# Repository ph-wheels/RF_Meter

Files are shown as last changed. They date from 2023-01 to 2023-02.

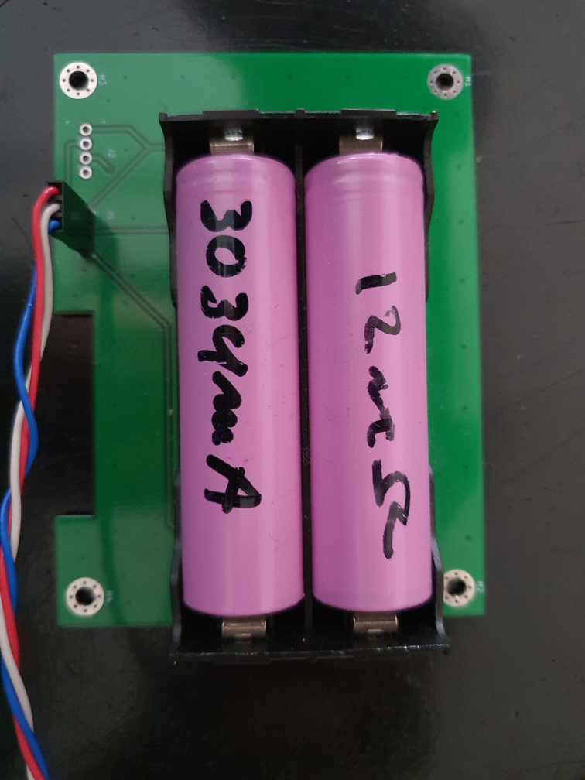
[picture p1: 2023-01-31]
images/battery_brd.png

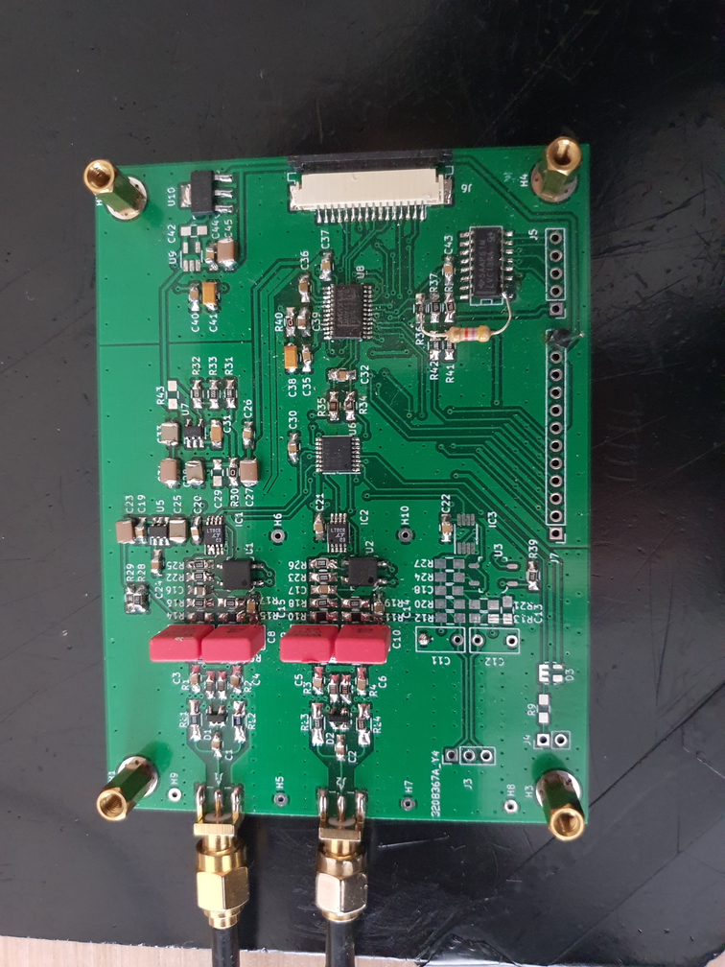
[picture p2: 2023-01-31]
images/adc_brd.png

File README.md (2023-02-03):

# RF_Meter
dual channel rf meter (work in progress)

This project started off with a question concerning replacement or source for
suitable detector diodes for the Boonton RF Millivolt meter quite a few months ago.
As a result of that, the idea was born to create a millivolt and/or power meter
using one of the modern ADC chips available today and since that time a few test
drawning and PCB where used in the process to the current V5 of the ADC board.
This project has been a combined effort with Jacques (ve2azx, http://www.ve2azx.net),
who already had developped a replacement board for the Boonton series of millivolt/
power meter as to fixed the issue with the mechanical chopper, without his valued
contribution, experiance, feedback and high precision RF measurement this project
would never exist.

The current design is based to 2 main PCB's and a battery board which also provides
some shielding to ADC board when mounted on top off it.

The control board consist of a connection to battery board, a flatcable connection
to ADC board and uart connection (ttl level) to external usb serial interface.
The board has and ESP32 MCU chip, which can be flashed via the USB serial interface,
will display info on the LCD screen (3.5" 480x240), monitors changes of the rotary
switch, touch screen, on-board push buttons and read/controls behaviour of the ADC
board. The RF Meter is battery powered and should be capable to provide adequate power
for several hours from 2x 2000 mAh or larger capacity batteries, optional board space
is provided to house a BMS unit and can be charged by the 2S 1A battery charger module
or via a barrel jack socket to deliver power via on-board regulator (3V3) to the MCU and
LCD screen.

The ADC board consist of 2 SMA and a flatcable connection to the control board,
optionally a connection to a 2 pin Amphenol connector, simular to the Boonton instruments.
This board holds 3 main area's being 3x input circuit, multiplexer with the ADC chip and the
voltages / reference sources with some control to switch attenuator and optional panel leds.
The input circuits for channels A/B are terminated with 50 Ohm followed by detector circuit
and attenuator, which is used to obtain a +23dBm range, into a differential low noise x1
amplifier, channel C (with it's components populated) only has the differential 5M6 resistors, the
attenuator and differential low noise x1 amplifier and is therefore not be a 50 Ohm input source.

Project status has been closed for now as we have finished our mean development goals being:
- a battery powered, using modern chips with large enough display making it a usable instrument
- a less than -55 dBm and up to +23 dBm input range
- a frequency range of less then 10 MHz upto in excess of 1 GHz
- an auto range mechanism in place over entire input range
- mechanism in place to load and maintain correction tables in none volatile memory

One area left for improvement is the option to obtain differential power reading between channel
B - A which kind of works (reasonably well within the lower 2 ranges) but will be slower in it's
update frequency then we expected it to be.

Future plans currently don't exist other then having an update schematic in place base on a dual
ADC chip approach which will speedup the channel B - A mode by factor 2x to 3x BUT this will yield
into a higher build cost due to extra ADC and the SSR / Mux chip.

Suggestion as how to build can be found in due time in folder 'Build' which will provide info and
steps to build the ADC and Control board and best practice to test and put each board into operation.

Paul	(PE1FCB (ex))

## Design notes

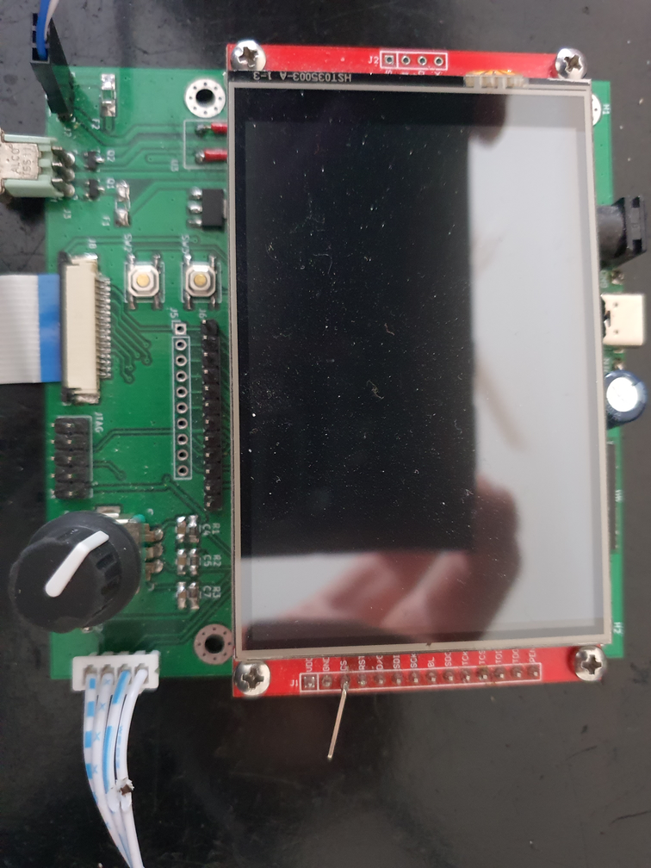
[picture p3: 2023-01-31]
images/control_display_brd.png

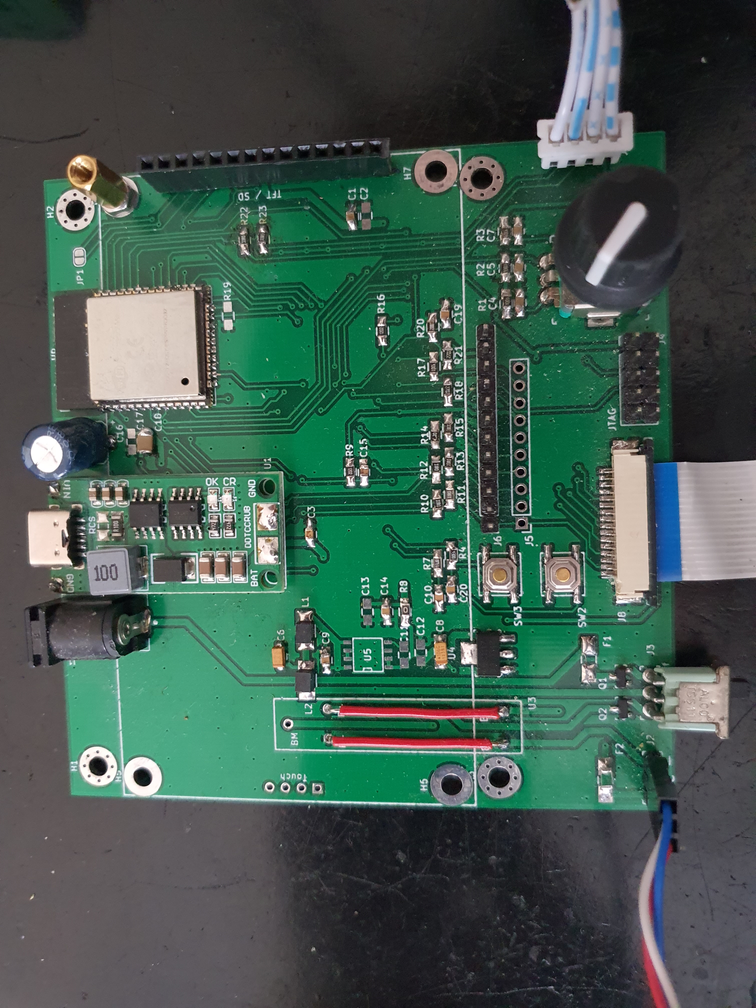
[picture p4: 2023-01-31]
images/control_brd.png

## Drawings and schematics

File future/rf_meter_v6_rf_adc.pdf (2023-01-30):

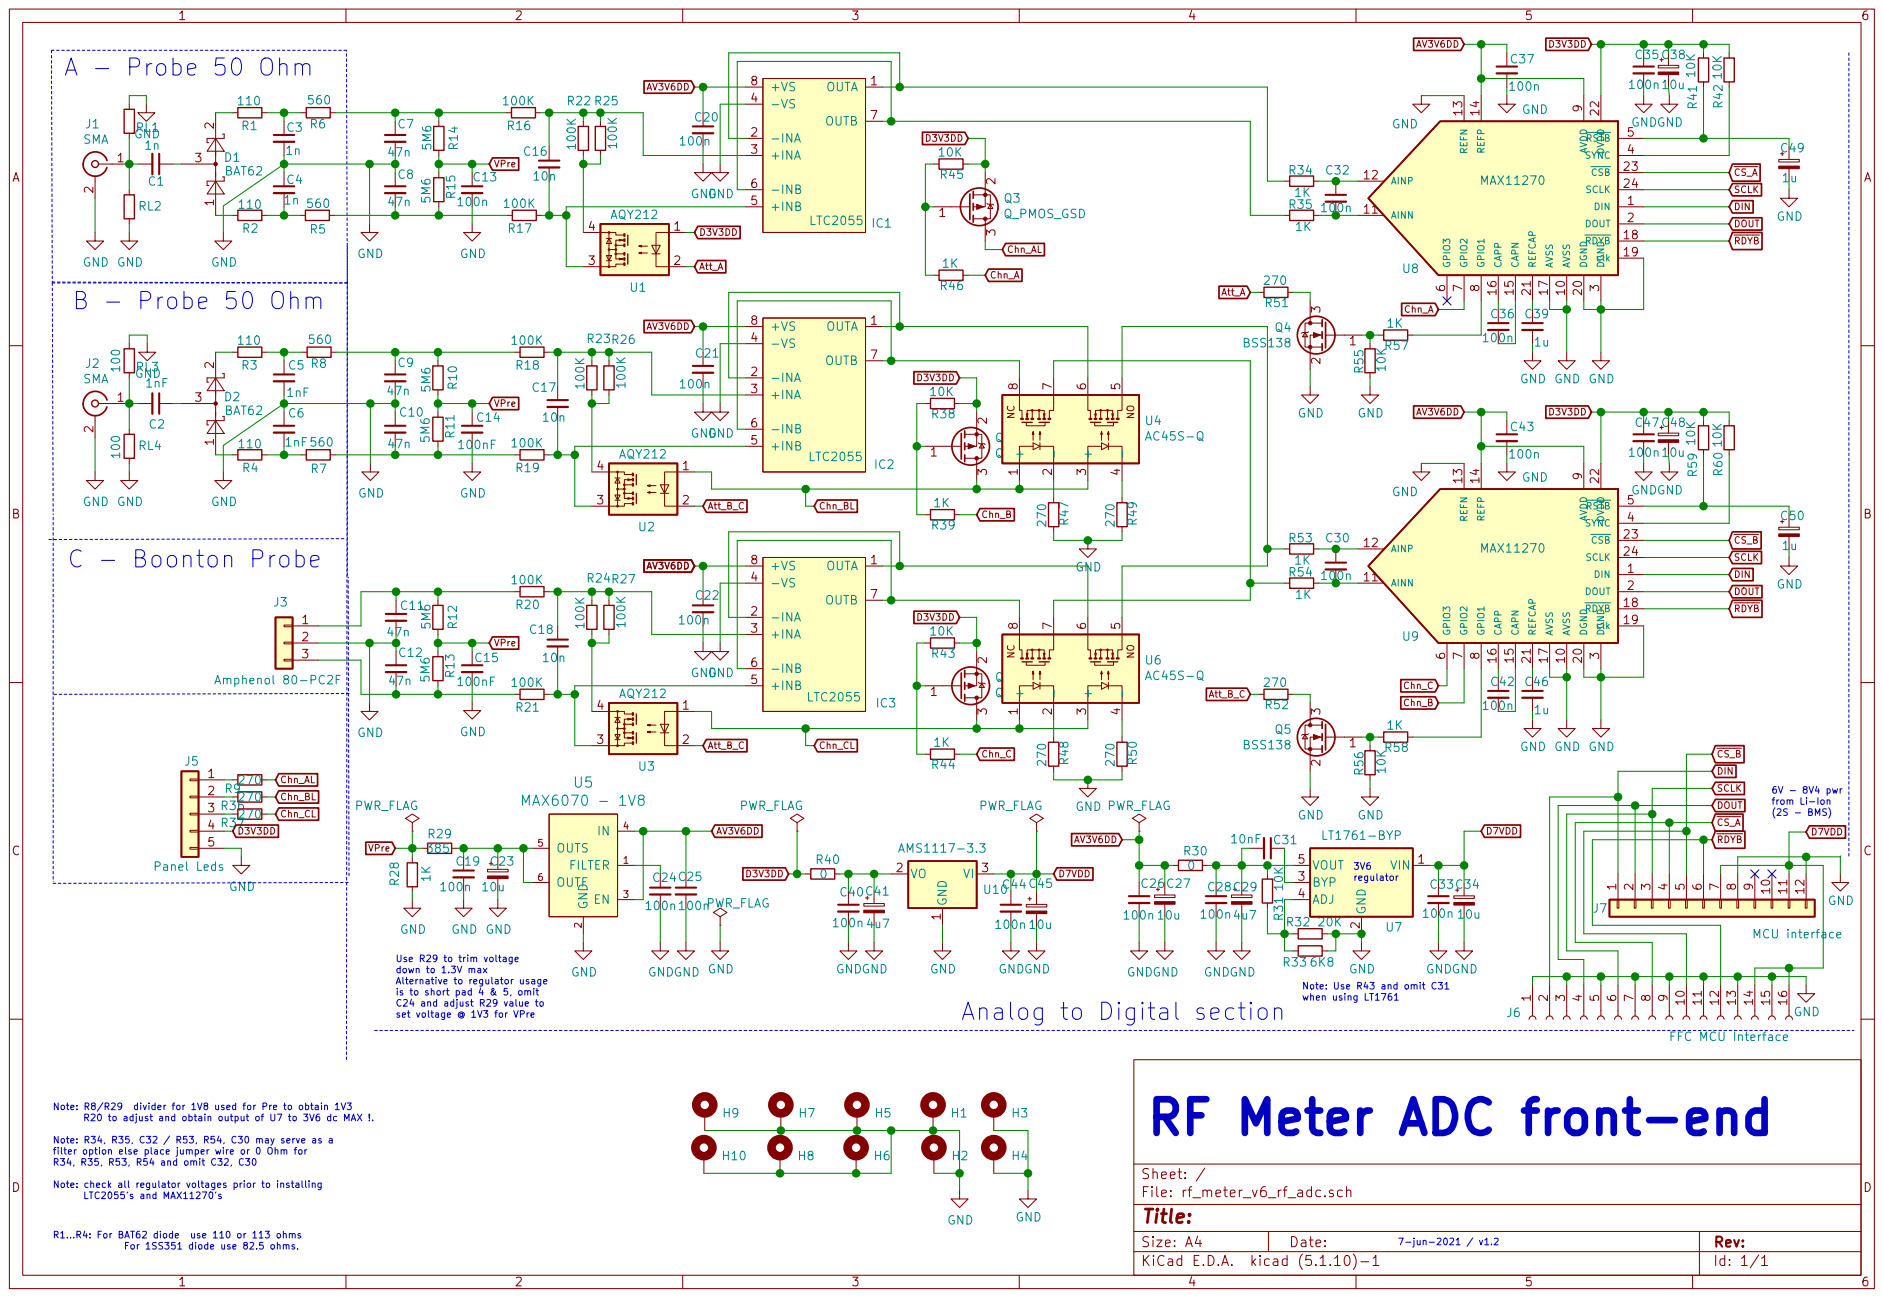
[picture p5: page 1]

7-jun-2021 / v1.2 Use R29 to trim voltage
down to 1.3V max Alternative to regulator usage

is to short pad 4 & 5, omit C24 and adjust R29 value to

Analog to Digital section

RF Meter ADC front-end

For 1SS351 diode use 82.5 ohms. Note: R8/R29 divider for 1V8 used for Pre to obtain 1V3
R20 to adjust and obtain output of U7 to 3V6 dc MAX !. Note: R34, R35, C32 / R53, R54, C30 may serve as a

filter option else place jumper wire or 0 Ohm for R34, R35, R53, R54 and omit C32, C30 Note: check all regulator voltages prior to installing

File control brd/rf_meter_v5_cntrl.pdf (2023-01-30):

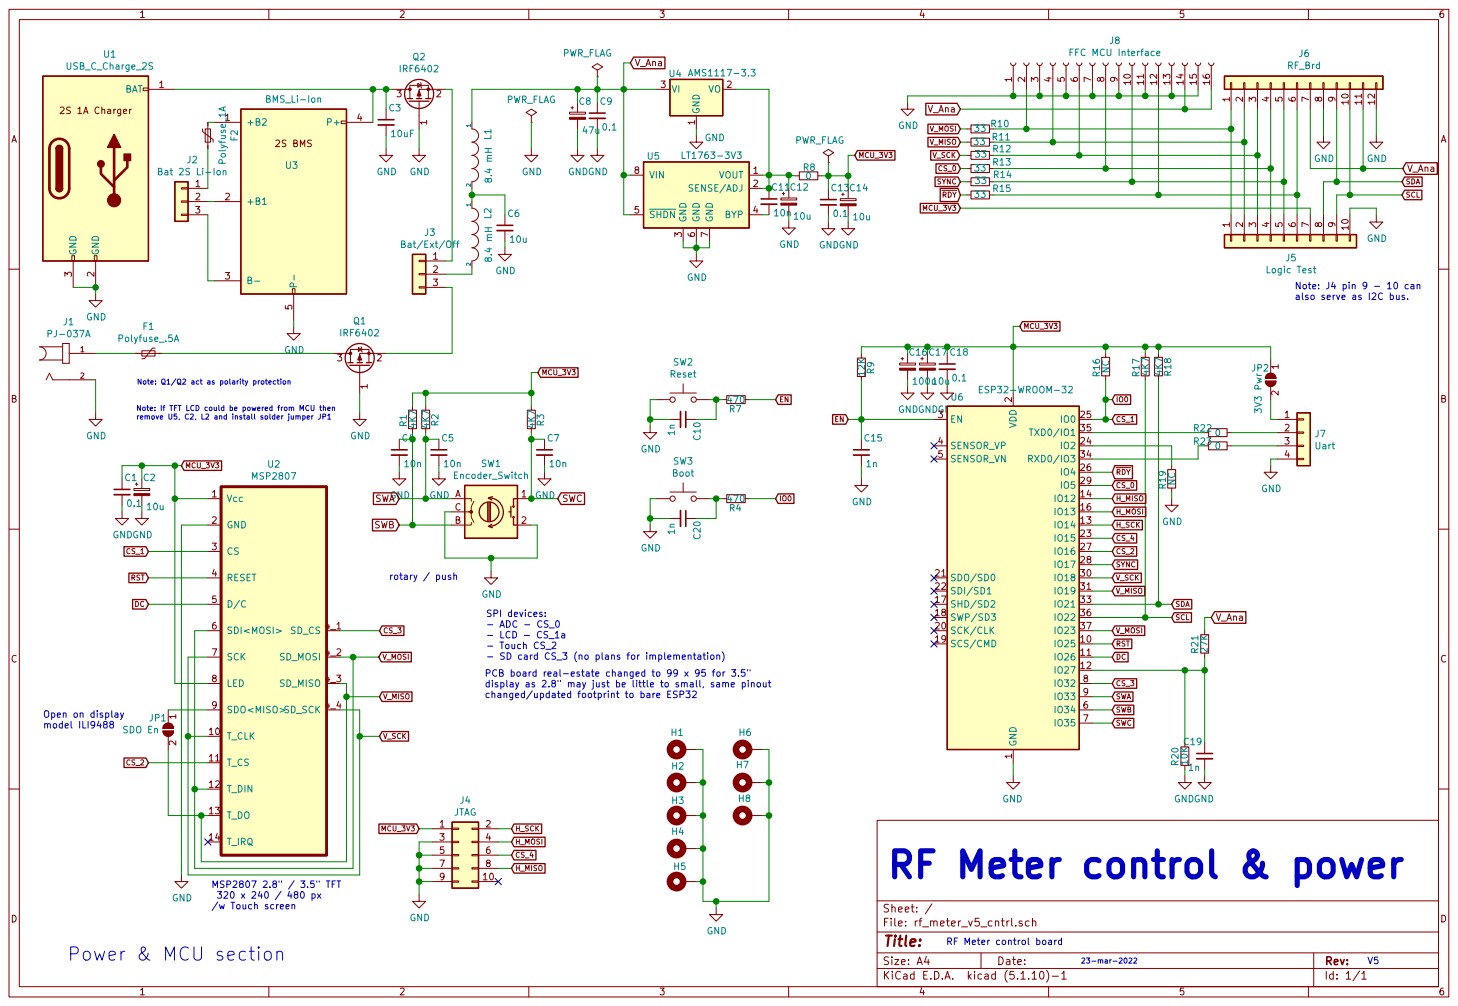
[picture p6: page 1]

also serve as I2C bus.

changed/updated footprint to bare ESP32 Note: Q1/Q2 act as polarity protection Note: If TFT LCD could be powered from MCU then

2 SCK/CLK 20 SDO/SD0 21 SDI/SD1 22

- LCD - CS_1a
- Touch CS_2
- SD card CS_3 (no plans for implementation)

display as 2.8" may just be little to small, same pinout

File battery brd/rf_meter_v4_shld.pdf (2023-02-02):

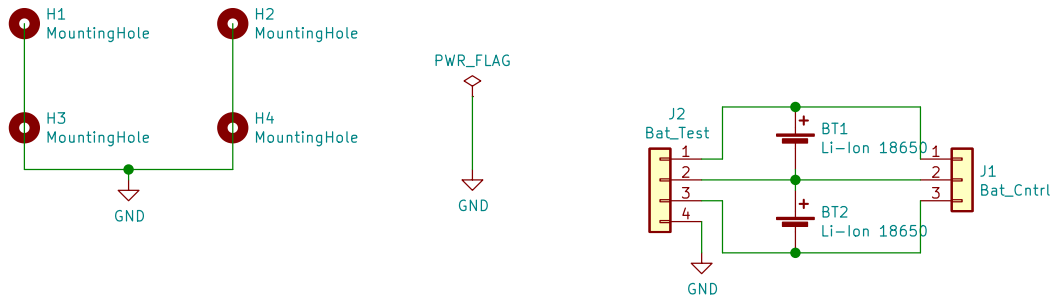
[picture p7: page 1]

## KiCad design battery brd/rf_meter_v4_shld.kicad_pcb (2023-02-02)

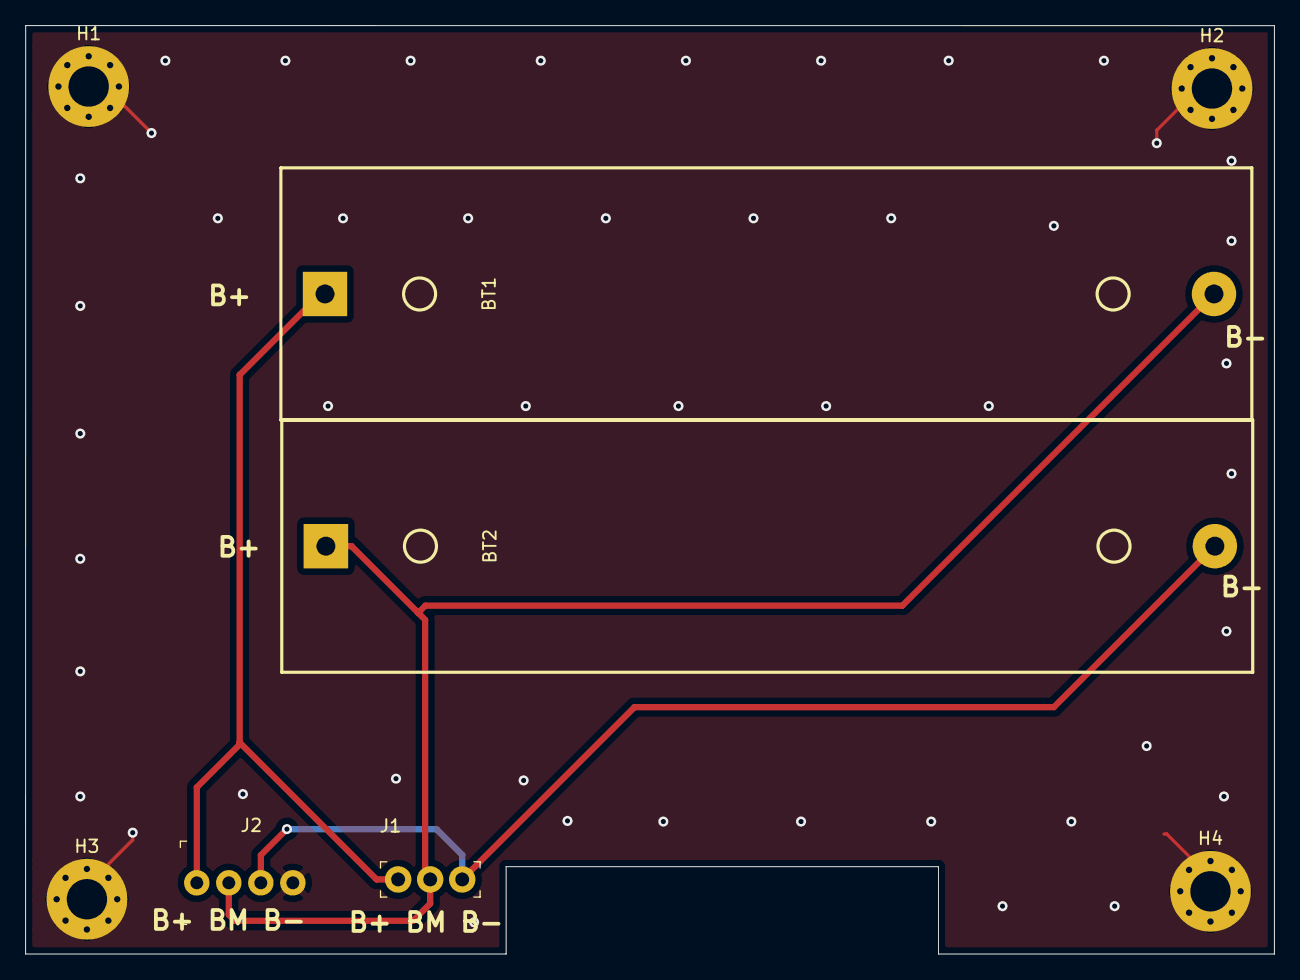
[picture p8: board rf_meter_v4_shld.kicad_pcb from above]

Board: 2 copper layers, 99.0 x 73.6 mm, 8 parts (0 on the bottom side), 4 nets.

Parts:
BT1, BT2: Li-Ion 18650; Battery_Holder_2S
H1, H2, H3, H4: MountingHole; MountingHole_3.2mm_M3_Pad_Via
J1: Bat_Cntrl; PinHeader_1x3_P2.54_Drill1.1mm
J2: Bat_Test; PinHeader_1x4_P2.54mm_Drill1.02mm

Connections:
GND: H1.1, H2.1, H3.1, H4.1, J2.4
unnamed: BT1.1, J1.1, J2.1
unnamed: BT1.2, BT2.1, J1.2, J2.2
unnamed: BT2.2, J1.3, J2.3

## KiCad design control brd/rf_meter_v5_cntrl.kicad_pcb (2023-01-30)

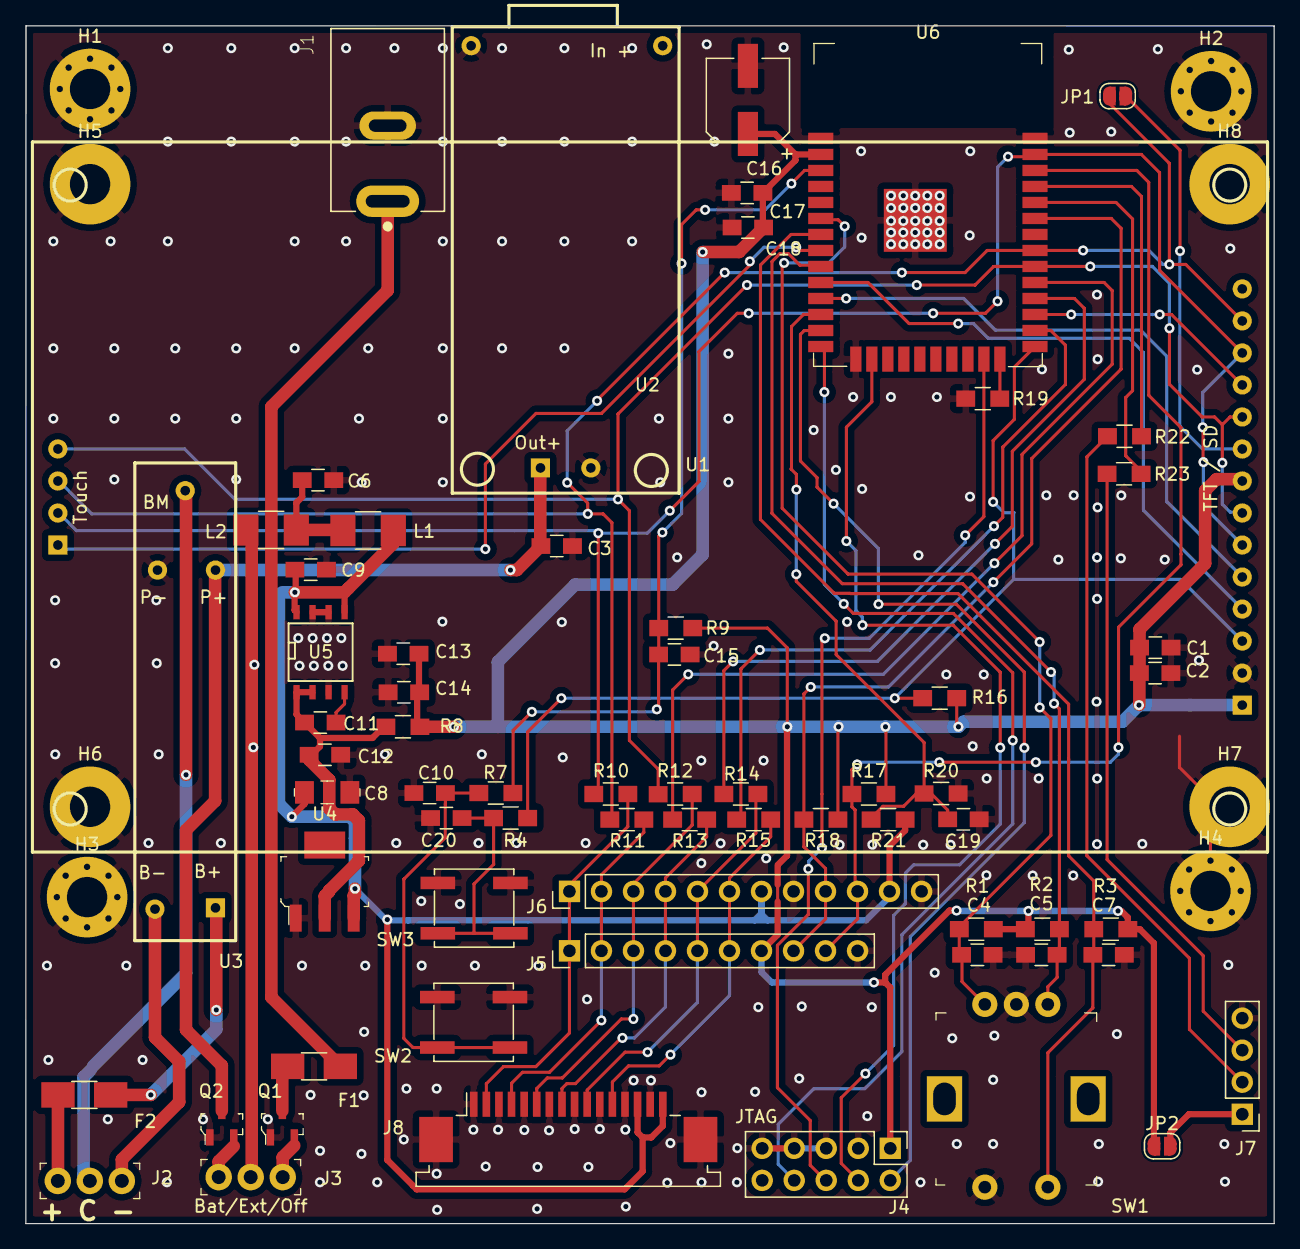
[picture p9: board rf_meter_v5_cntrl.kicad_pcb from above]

Board: 2 copper layers, 99.0 x 95.0 mm, 74 parts (0 on the bottom side), 53 nets.

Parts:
C1, C9, C13, C18: 0.1; C_0805_HandSoldering
C2, C6, C12, C14, C17: 10u; C_0805_HandSoldering
C3: 10uF; C_0805_HandSoldering
C4, C5, C7, C11: 10n; C_0805_HandSoldering
C8: 47u; 1206
C10, C15, C19, C20: 1n; C_0805_HandSoldering
C16: 100u; CP_Elec_6.3x5.7
F1: Polyfuse_.5A; Fuse_SMD1206_HandSoldering
F2: Polyfuse_1A; Fuse_SMD1206_HandSoldering
H1, H2, H3, H4: MH; MountingHole_3.2mm_M3_Pad_Via
H5, H6, H7, H8: MH; MountingHole_3.2mm_M3_Pad
J1: PJ-037A; CUI_PJ-037A
J2: Bat 2S Li-Ion; PinHeader_1x3_P2.54_Drill1.1mm
J3: Bat/Ext/Off; PinHeader_1x3_P2.54_Drill1.1mm
J4: JTAG; Pin_Header_Straight_2x05_Pitch2.54mm
J5: Logic Test; Pin_Header_Straight_1x10_Pitch2.54mm
J6: RF_Brd; Pin_Header_Straight_1x12_Pitch2.54mm
J7: Uart; Pin_Header_Straight_1x04_Pitch2.54mm
J8: FFC MCU Interface; TE_1-84952-6_1x16-1MP_P1.0mm_Horizontal
JP1: SDO En; SolderJumper-2_P1.3mm_Open_RoundedPad1.0x1.5mm
JP2: 3V3 Pwr; SolderJumper-2_P1.3mm_Open_RoundedPad1.0x1.5mm
L1, L2: 8.4 mH; L_1210_HandSoldering
Q1, Q2: IRF6402; SOT-23-3
R1, R2, R3, R17, R18: 4K7; R_0805_HandSoldering
R4, R7: 470; R_0805_HandSoldering
R8, R22, R23: 0; R_0805_HandSoldering
R9: 12K; R_0805_HandSoldering
R10, R11, R12, R13, R14, R15: 33; R_0805_HandSoldering
R16, R19: NC; R_0805_HandSoldering
R20: 10K; R_0805_HandSoldering
R21: 27K; R_0805_HandSoldering
SW1: Encoder_Switch; Rotary_Encoder_Switched_PEC11R
SW2: Reset; SW_SPST_EVPBF
SW3: Boot; SW_SPST_EVPBF
U1: USB_C_Charge_2S; USB-C_Charge_2S
U2: MSP2807; 3.5_TFT
U3: BMS_Li-Ion; HX-2S-A10
U4: AMS1117-3.3; SOT-223-4
U5: LT1763-3V3; SOIC-8-N
U6: ESP32-WROOM-32; ESP32-WROOM-32D

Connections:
CS_0: R13.1, U6.29
CS_1: R4.1, R16.2, U2.3, U6.25
CS_2: U2.11, U6.27
CS_3: U2.4_1, U6.8
CS_4: J4.6, U6.23
DC: U2.5, U6.11
EN: C15.1, R7.1, R9.2, U6.3
GND: C1.2, C2.2, C3.2, C4.2, C5.2, C6.2, C7.2, C8.2, C9.2, C10.2, C12.2, C13.2, C14.2, C15.2, C16.2, C17.2, C18.2, C19.2, C20.2, H1.1, H2.1, H3.1, H4.1, H5.1, H6.1, H7.1, H8.1, J1.2, J4.3, J4.5, J4.7, J4.9, J5.10, J6.8, J6.12, J7.4, J8.1, J8.3, J8.5, J8.7, J8.9, J8.11, J8.13, J8.15, J8.MP, Q1.1, Q2.1, R19.2, R20.2, SW1.2, SW1.C, SW2.1, SW3.1, U1.2, U1.3, U2.2, U3.5, U4.1, U5.3, U5.6, U5.7, U6.1, U6.15, U6.38, U6.39
H_MISO: J4.8, U6.14
H_MOSI: J4.4, U6.16
H_SCK: J4.2, U6.13
MCU_3V3: C1.1, C2.1, C13.1, C14.1, C16.1, C17.1, C18.1, J4.1, J5.7, JP2.1, R1.1, R2.1, R3.1, R8.1, R9.1, R16.1, R17.1, R18.1, U2.1, U2.8, U6.2
unnamed: C3.1, Q2.3, U1.1, U3.4
unnamed: C6.1, L1.2, L2.1
unnamed: C10.1, R7.2, SW2.2
unnamed: C11.1, C12.1, R8.2, U4.2, U5.1, U5.2
unnamed: C11.2, U5.4
unnamed: C19.1, R20.1, R21.2, U6.12
unnamed: C20.1, R4.2, SW3.2
unnamed: F1.1, Q1.3
unnamed: F1.2, J1.1
unnamed: F2.1, J2.1
unnamed: F2.2, U3.1
unnamed: J2.2, U3.2
unnamed: J2.3, U3.3
unnamed: J3.1, Q2.2
unnamed: J3.2, L2.2
unnamed: J3.3, Q1.2
unnamed: J5.1, J6.1, J8.2, R10.2
unnamed: J5.2, J6.2, J8.4, R11.2
unnamed: J5.3, J6.3, J8.6, R12.2
unnamed: J5.4, J6.4, J8.8, R13.2
unnamed: J5.5, J6.5, J8.10, R14.2
unnamed: J5.6, J6.6, J8.12, R15.2
unnamed: J7.1, JP2.2
unnamed: J7.2, R22.1
unnamed: J7.3, R23.1
unnamed: JP1.1, U2.9
unnamed: R19.1, U6.24
unnamed: R22.2, U6.35
unnamed: R23.2, U6.34
RST: U2.4, U6.10
SCL: J5.9, J6.10, R17.2, U6.36
SDA: J5.8, J6.9, R18.2, U6.33
SWA: C5.1, R2.2, SW1.A, U6.9
SWB: C4.1, R1.2, SW1.B, U6.6
SWC: C7.1, R3.2, SW1.1, U6.7
SYNC: R14.1, U6.28
V_Ana: C8.1, C9.1, J6.7, J6.11, J8.14, J8.16, L1.1, R21.1, U4.3, U5.5, U5.8
V_MISO: JP1.2, R11.1, U2.4_3, U2.13, U6.31
V_MOSI: R10.1, U2.4_2, U2.6, U2.12, U6.37
V_SCK: R12.1, U2.4_4, U2.7, U2.10, U6.30
~RDY: R15.1, U6.26

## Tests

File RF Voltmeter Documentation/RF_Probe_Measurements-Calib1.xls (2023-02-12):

RF Voltmeter |  |  |  | Jacques Audet
RF PROBE Measurements |  |  |  | 2023-02-12
 |  |  | RF Probe dBm vs VDC input
 |  | Measured data at10 MHz using BAT62 diode
 |  | ADC Range Switching Points
 |  | Ref V | PGA Gain: | 128 |  | 4 |  | 1
 |  | 3.6 | dBm IN: | -60 | -25 | -26 | -5 | -6 | 15 | Max / Min X1 buffer out | Per Spec. Max / Min PGA out @ X2---128
 |  | ADC IN from RF probe µV: |  | 1.72 | 5500 | 4400 | 247000 | 210000 | 3000000
 |  | PGA max. output VDC |  | 1.80011 | 2.15 | 1.809 | 2.294 | 1.91 | 3.30 | 3.3 | 2.3
 |  | PGA min. output VDC |  | 1.79989 | 1.45 | 1.791 | 1.306 | 1.70 | 0.30 | 0.3 | 0.3
 |  | Gain | µV/bit
 |  | 1 | 0.2145767212 |  |  |  | 1227000 | 1057700 | 15390000
 |  | 2 | 0.1072883606
 |  | 4 | 0.0536441803 |  | 92620 | 74000 | 4130000 | 3559000
 |  | 8 | 0.02682209015
 |  | 16 | 0.01341104507
 |  | 32 | 0.006705522537
 |  | 64 | 0.003352761269
 |  | 128 | 0.001676380634 | 1000 | 2959000 | 2362000
V4 ADC / CTRL |  |  | MEASURED DATA |  | CableLoss = | 0.2 | dB | Ftest = 10 MHz |  |  |  |  | Calculation of coefficients: Ax
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

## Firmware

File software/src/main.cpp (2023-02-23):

#include <Arduino.h>
#include <cstdio>
#include <cmath>
#include <cstring>
#include <cstring>
#include <SPI.h>
#include <stdint.h>
#include <MAX11270.h>
#include <Ticker.h>
#include <Preferences.h>
#include <Clickencoder.h>
#include <main.h>
#include <Menu.h>
#include <TFT_eSPI.h>     // Hardware-specific library for TFT
#include <Free_Fonts.h>
#include "WiFi.h" 
#include <esp_wifi.h>
#include <esp_bt.h>
#include <SerialCommand.h>
#include <ArduinoJson.h>
#include <stdlib.h>

/* Usefull links & software & general info partially used for this application
 * Link to usefull max11214 driver : https://github.com/LucasEtchezuri/Arduino-MAX11214
 * How to flash esp32: https://www.espressif.com/en/support/download/other-toolsS
 * Usefull link on flash usage: https://github.com/espressif/arduino-esp32/blob/
 * https://forum.arduino.cc/t/serial-input-basics-updated/382007/3
 * master/libraries/Preferences/examples/StartCounter/StartCounter.ino
 * Usefull link on TFT usage: https://www.youtube.com/watch?v=rq5yPJbX_uk
 * Usefull link on dual SPI usage: https://github.com/espressif/arduino-esp32/blob/
 * Usefull link on battery capacity level for Li-Ion type 16820: https://www.youtube.com/watch?v=mfiRJ1qgToc
 * master/libraries/SPI/examples/SPI_Multiple_Buses/SPI_Multiple_Buses.ino
 * master/examples/SerialCommandHardwareOnlyExample/SerialCommandHardwareOnlyExample.ino
 * https://www.allaboutcircuits.com/technical-articles/getting-started-with-openocd-using-ft2232h-adapter-for-swd-debugging/
 * Usefull link on https://community.platformio.org/t/debugging-esp32-how/4499
 * Usefull link on Polymomial Regression https://www.statology.org/polynomial-regression-excel/
 * Usefull link on rotary encoder and menu:
 * https://github.com/im-pro-at/ESP32_ReflowOvenController/tree/master/ReflowController
 * potentially patch C:\Users\paul\.platformio\packages => esp32-hal-timer.c -> add volatile keyword to structs
 * for now timer interrupt is set @ 10ms interval
 * an alternative encoder implementation: https://github.com/RalphBDacon/226-Better-Rotary-Encoder---no-switch-bounce
 * /blob/main/YetAnotherRotaryEncoder/YetAnotherRotaryEncoder.ino
 * but it's laking an push button 
 * https://savjee.be/2019/12/esp32-tips-to-increase-battery-life/
 * https://github.com/kroimon/Arduino-SerialCommand/tree/master/examples
 * https://github.com/ppedro74/Arduino-SerialCommands
 * for personal reference only:
 * python  esptool.py --chip esp32 --port com6 erase_flash
 * python  esptool.py --chip esp32 --port com6 --baud 460800 write_flash -z 0x1000 C:\Users\paul\Downloads\esp32-idf3-20191220-v1.12.bin
 * 
 */

/*
 * SW history:
 * 
 * 2.0b1  switched to dual value display, removed menu items, added uW
 *    b2  adjusted chan # from 0-2 to 1-3 & feedback
 *    b3  corrections as per feedback 11-12
 *    b4  enhancement on input termination
 *        corrections as per feedback 15-12
 *        ToDo => alternative method for dBm offset value
 *    b7  changed channel select to A, B, C
 *        added partial coding for B - A
 *    b8  completed B - A/C - A coding, modified selection / menu behaviour
 *        released for test by Jacques.
 *    b9  change as to avoid flickering on battery status update
 * 2.1b1  fixed some issue's on B-A/C-A, introduced dual click and term value
 *    b2  some more issue on dual channel, problems with correct readout of B
 *        send to Jacques for confirmation of either sw or hw problem
 *    b3  replace range 1 constants provided by Jacques
 * 2.2b1  changed adc handling to be interrupt driven as to elliminates delays
 *    b2  adjusted range of scanadc value, min = 100, max 500
 *    b3  finally, finally got the dual chan mode to work, reason wrong update of r_val
 *    b4  added support for second click to zero out B-A / C-A & disabled double click
 *    b5  move refence value r_val[] to global space, fixed A0 table issue
 *    b6  added a NoiseFloor parameter option as be able to stop displaying noise
 * 2.3b1  added attenuator controle
 *    b3  hw change -> changed r29 to 0 Ohm to reduce noise at very low levels
 *        added attenuator value compensation -> measure value * 5 = 14dBm
 *    b4  Updated the TFT_eSPI library as to obtain proper eSprite support
 *        implemented eSprite for Meter area
 *        Improved Helper function to utilize array instead of switch statement
 *    b5  Changed Battery voltage indication to remaining charge percentage
 *        & improved battery symbol
 *        Added bulk data upload routine to init nvs flash (L cmd)
 *    b6  Changed to PGA mode only and Vref to be 1.3 V
 * 
 *    ToDo: Implement usage of Sprite as to reduce screen flickering -> Done
 *          split usage of correction polynome / channel
 *          import option of data file to init flash_nvr for rf-meter
 *          general cleanup & remove unused coding parts
 * 2.4b1  We finally found odd range switching issue and move over to json load
 *        file for polynome values as to allow for more flexibility 
 *    b2  removed * 5 on high level as it will be compensated by polynome
 *    b3  aligned attenuator, so attenuator is enabled over full range 1
 *    b4  reduced spi clk from 20 to 18 MHz
 *    b5  redesign adc sampling to be event drive by interrupt sps 1.9 -> 508 mS
 *    b6  adjusted polynome array's size to be 5 elements, conversion routine will test
 *        for zero values to be skipped, improved flash screen to show proper version
 *        found issue on 13.01 dBm display --> no proper import of polynome jason file.
 *  2.5.0 version naming changed from 2.4b6 to 2.5.0
 *        revised auto_ranging as to deal with multi chan, multi range
 *        dual channel sample delay's been removed, some cleanup unused stuff
 *        naming for channels unified
 *  2.5.1 added test on flash data for polynomial, correctiopn data etc
 *        initial version for test & feedback
 *     .2 scanadc parameter remove as it became obsolete due to interrupt drive adc sampling
 *        renamed 'L' to 'LP' and added the 'LS' option to load Vref and battery ratio and sample rate
 *     .3 fixed range output to serial, added 'Flash Incorrect' notification on display, 
 *        removed dual channel debug messages, improved json load error message
 *     .4 increased serial timeout to 10sec, renamed variable flg / init at setup
 *     .5 Fixed odd behaviour on A0 corrections, re-arranged function requence solved issue
 *        todo -> zero button implementation
 *     .6 fixed issue with INF at startup with low level input (finally found it, value in array not defined !)
 *        added internal cal at startup and scan for average with no input signal
 *     .7 fixed min displayed value to be 30 adc counts, doing average offset for active channel
 *        added missing coding part on monitor output in case of averaging is active
 *     .8 fixed incorrect data issue on serial output, zero duration is now 10 sec, 0.0 is displayed as LOW
 *     .9 could same as .8 which was internal test usage, .9 released for off site tests
 *  2.6.0 added optio to tune # of samples vor zero offset operation
 *     .1 made several changes to the chk_autoRage function which was causing hangs and irratic data to display
 *     .2 removed dummy read delay on B - A / C - A as to speedup readout, seems to work ok.
 *     .3 back to dummy read delay as fast mode  didn't work properly, fixed some issue, startup with gain 1 / att on
 *     .4 adjusted channel selection timing for dual channel mode
 *     .5 corrected the issue of wrongly driving the attenuator
 *     .6 resolved issue of wrongly implementing correction factors over a reboot
 *     .7 forgot to track changes ... and lost them
 *     .8 changed implementation of chk_autorage function but still issue in a/b mode
 *     .9 changed chn_arr_init() to it's function default => lvl 2, att off
 */

#define M_Bar_Gain      25
#define MTR_FONT FSSB24
#define STS_FONT FSS9
#define splash_delay    2000
#define ADC_CLK         18        // ADC SPI pins in use
#define ADC_MISO        19        //
#define ADC_MOSI        23        //
#define ADC_CS          5         //
#define ADC_DRDY        4         // also used forhw interrupt on ADC ready
#define SDA             21        // I2C bus option pins, not used
#define CLK             22        //
#define ADC_SYNC        17        // added, define pin used by adc sync input, should be grounded
#define ADC_PIN         27        // used to measure battery voltage
#define ADC_RESOLUTION  16777215  // 
#define ADC_UNI_MAX     16700100  // used to signal upcoming overload
//#define ATT_HIGH        7334000   // attenuator switch points
//#define ATT_LOW         1312000   //
#define JSON_TIMEOUT  10000
#define VERSION 5
#define CHAN_A  0
#define CHAN_B  1
#define CHAN_C  2
#define off_size 60
#define avg_Max 6
#define json_size 2000  //1536
#define ADC_DELTA 1
// auto ranger switching points
#define r1_r2_dn 129900
#define r2_r3_dn 74000
#define r2_r1_up 4130000
#define r3_r2_up 2959000

//#define nvs_erase 1
//#define nvr_debug 1       // used for profile value display
//#define mnu_debug 1       // used for menu render time display
//#define lcd_debug 1       // used touch screen calibration values
//#define raw_mode  1       // used to bypass polynome corrections
//#define dbm_debug 1
//#define cal_debug 1
//#define ply_debug 1       // polynome test / debug
//#define dch_debug 1
//#define chk_debug 1
//#define car_debug 1       // chk_autorange function

#if (nvs_erase)
  #include <nvs_flash.h>
#endif

hw_timer_t * encodertimer = NULL;
portMUX_TYPE timerMux = portMUX_INITIALIZER_UNLOCKED;
portMUX_TYPE mux = portMUX_INITIALIZER_UNLOCKED;

MAX11270 adc;                 // get max11270 object instance
Preferences PREF;

int32_t AdcResp = 0;

bool sampling = false;
bool pga_ena  = false;
bool cmd_echo = false;
bool dbg_mon  = false;
bool dsp_cln  = false;
bool secClick = false;
bool conv_rdy = false;
bool adc_rdy  = false;
bool cal_int  = false;
bool avg_Act  = false;
bool smp_Fast = false;
bool dm_debug = false;
int8_t cal_stp = 0;
int8_t avg_Val = 4;
int8_t avg_idx = 0;
int32_t avg_smp[6][3] = {0, 0, 0, 0, 0, 0,
                         0, 0, 0, 0, 0, 0,
                         0, 0, 0, 0, 0, 0};
uint16_t sps_delay[4] = {0,0,0,0};
static bool att_sts[3] = {false, false, false};
int8_t ADC_S_Chan  = 0;
int8_t ADC_M_Chan  = 0;
int8_t dsp_cnt     = 30;
int8_t single_mode = 0;

double Bat_lvl = 0.0;
float  Bat_Ratio = 3.21;

double off_value = 0.0;
int16_t low_lvl = 0;

double vac = 0.0;
double dbm = 0.0;
volatile static double dbm_a = 0.0;
volatile static double dbm_b = 0.0;
uint32_t Adc_a = 0;
uint32_t Adc_x = 0;

float    ltx = 0;                         // Saved x coord of bottom of needle
uint16_t osx = 160, osy = 160;            // Saved x & y coords

char helper_arr[18][10] = {
      "dBm", "Vac", "mVac", "uVac", "mW", "uW", "dB Rel", "dBm Off", "mW Off",
      "uW", "", "dB", "CH: A", "CH: B", "CH: C", "CH: B - A", "CH: C - A", "?????"};

int gains[3] = {0, 2, 7};                 // gain range to actual gain
int value[6] = {0, 0, 0, 0, 0, 0};
int old_value[6] = {-1, -1, -1, -1, -1, -1};
uint32_t off_val[3] = {0, 0, 0};
int d = 0;

static uint32_t lastAdc[3] = {};          // previous adc value for channel
static int r_val[3] = {};                 // range value for chan
static int R[3] = {1, 2, 3};              // range translation
//static bool N[3] = {false, false, false}; // noisy signal flag
static uint16_t dly_cnt;

double Radc = 2.1529198976e-7;    // Resolution = Vavdd / 16777215
int S = 0;                        // status / controle registers on/off
int C = 0;                        // calibration registers on/off

volatile bool Disable_flg;
volatile uint8_t dual_step;
volatile static bool a_x_mode = false;
volatile bool rotaryEncoder = false;
volatile bool rotaryPush = false;
int rotationCounter = 1;
unsigned long lastButtonPress = 0;
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

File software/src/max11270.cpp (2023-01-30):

#include "Arduino.h"
#include "MAX11270.h"
#include "SPI.h"

/* with credits to: Lucas Etchezuri who created a library for max11214
 * which with some modifications could be addapted for max11270 (cheaper version)
 */

//#define max_debug

#define settings SPISettings(5000000, MSBFIRST, SPI_MODE0)
SPIClass * vspiMax = NULL;

MAX11270::MAX11270()
{
}

void MAX11270::writeRegister(uint8_t address, uint8_t value)
{
  digitalWrite(MAX11270_CS_PIN, LOW);
  vspiMax->beginTransaction(settings);
  delayMicroseconds(1);
  vspiMax->transfer(CMD_WRITE_REGISTER | (address << 1));
  vspiMax->transfer(value);
  delayMicroseconds(1);
  vspiMax->endTransaction();
  digitalWrite(MAX11270_CS_PIN, HIGH);
  #ifdef max_debug
    Serial.printf("Reg: %02x, Val: %02x\n", address, value);
  #endif
}

/* added as to be able to write spi based calibration registers */
void MAX11270::writeSpiRegister(uint8_t address, uint32_t value)
{
  digitalWrite(MAX11270_CS_PIN, LOW);
  vspiMax->beginTransaction(settings);
  delayMicroseconds(1);
  vspiMax->transfer(CMD_WRITE_REGISTER | (address << 1));
  uint8_t val1 = value >> 16;
  vspiMax->transfer(val1);
  uint8_t val2 = value >> 8;
  vspiMax->transfer(val2);
  vspiMax->transfer(value);
  delayMicroseconds(1);
  vspiMax->endTransaction();
  digitalWrite(MAX11270_CS_PIN, HIGH);
  #ifdef max_debug
    Serial.printf("Reg: %02x, Val: %02x\n", address, value);
  #endif
}

void MAX11270::execCal(uint8_t address, uint8_t value)
{
  digitalWrite(MAX11270_CS_PIN, LOW);
  vspiMax->beginTransaction(settings);
  delayMicroseconds(1);
  vspiMax->transfer(CMD_WRITE_REGISTER | (address << 1));
  vspiMax->transfer(value);
  delayMicroseconds(1); //00
  vspiMax->transfer(CMD_CALIBRATE);
  delayMicroseconds(250000);
  vspiMax->endTransaction();
  digitalWrite(MAX11270_CS_PIN, HIGH);
  #ifdef max_debug
    Serial.printf("Reg: %02x, Val: %02x,\nCmd: %02x\n", address, value, CMD_CALIBRATE);
  #endif
}

uint8_t MAX11270::readRegister(uint8_t address)
{
  digitalWrite(MAX11270_CS_PIN, LOW);
  vspiMax->beginTransaction(settings);
  delayMicroseconds(1);
  vspiMax->transfer(CMD_READ_REGISTER | (address << 1));
  uint8_t data = vspiMax->transfer(SPI_MASTER_DUMMY);
  delayMicroseconds(1);
  vspiMax->endTransaction();
  digitalWrite(MAX11270_CS_PIN, HIGH);
  return data;
}

uint32_t MAX11270::readRegister24(uint8_t address)
{
  digitalWrite(MAX11270_CS_PIN, LOW);
  vspiMax->beginTransaction(settings);
  delayMicroseconds(1);
  vspiMax->transfer(CMD_READ_REGISTER | (address << 1));
  uint8_t data = vspiMax->transfer(SPI_MASTER_DUMMY);
  uint32_t val = data << 16;
  data = vspiMax->transfer(SPI_MASTER_DUMMY);
  uint32_t val2 = data << 8;
  uint32_t val3 = vspiMax->transfer(SPI_MASTER_DUMMY);
  delayMicroseconds(1);
  vspiMax->endTransaction();
  digitalWrite(MAX11270_CS_PIN, HIGH);
  return (val | val2 | val3);
  return 0;
}
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
